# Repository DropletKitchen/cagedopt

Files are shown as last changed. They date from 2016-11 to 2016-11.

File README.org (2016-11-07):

* Microfluidics Imaging Rigs with Caged Optics

*This page describes how to build simple optics rigs for microfluidics applications based on professional-grade caged optics sytems and scientific cameras.*

This is a [[https://DropletKitchen.github.io][DropletKitchen]] project.

If not stated otherwise, the designs and documentation in this repository
is Copyright (c) 2016 Martin Fischlechner and DropletKitchen Contributors,
and made available under a
[[https://creativecommons.org/licenses/by/4.0/][Creative Commons Attribution 4.0 International (CC BY 4.0)]] License.
** Introduction
This project shows one way to package caged optics into systems with a
small footprint and highly functional design. The example here is a
simple microscope-setup for microfluidics experimentation.  Instead of
using an optics table, or an all-metal optics breadboard, a
combination of laser-cut 5mm acrylic sheets with M6 nuts and bolts are
used to assemble rigid and customized optical instruments. The system
uses a simple, magnetic kinematic design for the x,y,z-stage and a
high-power LED with cheap plastic focusing optics for illumination.
The optics is based on an infinity-corrected objective, a lens and a
global-shutter CCD or CMOS-camera to obtain videos or images. The
output of an infinity-corrected objective (they usually have an
'infinity' symbol engraved) is a parallel beam of light. It therefore
needs a lens to create an image. The advantage is that between the
objective and the lens many optic components can be placed; the design
can therefore also be used as a starting point for more complex
setups, e.g.  for measuring fluorescence. To get an idea which optics
components are available and how much they cost, have a look at the
websites of optics companies, for example Thorlabs
(https://www.thorlabs.com/navigation.cfm).

#+CAPTION: Image of the rig at several stages of the build. A] bottom plate with the optics and an LED-driver enclosed in a little box. B] plate with LED and magnets to hold the stage. This part is used to immobilise the optics by clamping. C] XYZ-stage: Z and tilt is adjusted with three optics screws. X-Y movement is controlled with an inexpensive xy-stage. D] the fully assembled rig.
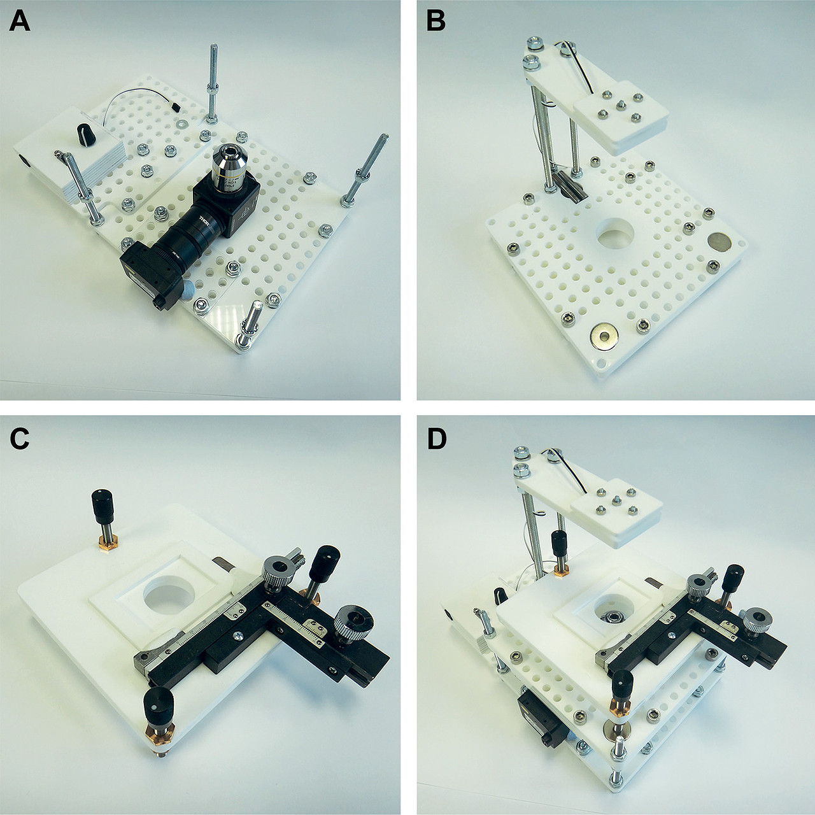
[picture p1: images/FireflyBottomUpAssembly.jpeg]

#+BEGIN_QUOTE
Image of the rig at several stages of the build. A] bottom plate with
the optics and an LED-driver enclosed in a little box. B] plate with
LED and magnets to hold the stage. This part is used to immobilise the
optics by clamping. C] XYZ-stage: Z and tilt is adjusted with three
optics screws. X-Y movement is controlled with an inexpensive
xy-stage. D] the fully assembled rig.
#+END_QUOTE

** Design
The model ([[./files/RigCageOpticsOpenSCAD.scad]]) was first developed in
openSCAD (http://www.openscad.org/) and sliced for lasercutting. Later
modifications were done in a .dxf-file with Draftsight
(http://www.3ds.com/products-services/draftsight-cad-software/free-download/). Starting
with a 3D-model is convenient to play with overall dimensions and
shapes, but the design is quicker to modify in 2D-CAD at later stages
([[./files/RigCageOpticsPartsForCutting.dxf]]). The standard fixtures for
optics on optics tables are M6, spaced 25mm apart. To have a flexible
way of mounting (additional) parts, holes of 6mm in diameter with a
spacing of 12.5mm (center to center) are additionally embedded into
the design where possible. This makes setups adaptable and extendable.

#+CAPTION: Left: 3D-model in openSCAD. Right: Parts for laser cutting.
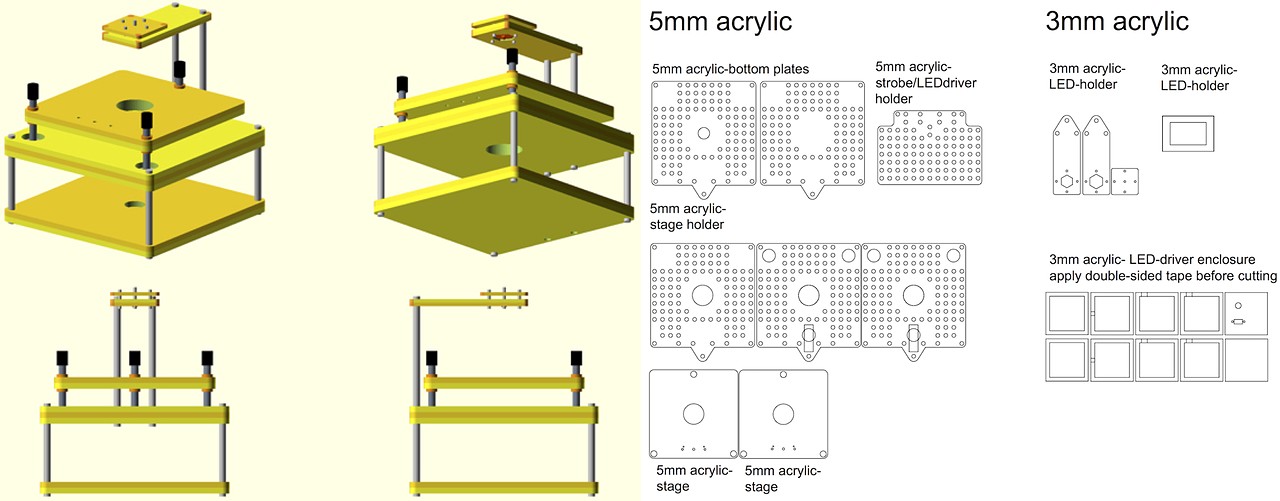
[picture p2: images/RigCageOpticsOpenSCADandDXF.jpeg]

#+BEGIN_QUOTE
Left: 3D-model in openSCAD. Right: Parts for laser cutting.
#+END_QUOTE
** Materials

| Item                                                                  |          number | bought from               | part number    | approx cost (£/euro) |
|-----------------------------------------------------------------------+-----------------+---------------------------+----------------+----------------------|
| Structural components                                                 |                 |                           |                |                      |
|-----------------------------------------------------------------------+-----------------+---------------------------+----------------+----------------------|
| M6 Hex Screws (different lengths, eg l=16,20,25,30mm for flexibility) |            many | RS or other hardware shop |                |                   NA |
| M6 Nuts, Washers, 'shake-proof washers'                               |            many | RS or other hardware shop |                |                   NA |
| M6 Threaded Rods                                                      |     4x (~100mm) | hardware shop             |                |                   NA |
| M6 Threaded Rods                                                      |     3x (~150mm) | hardware shop             |                |                   NA |
| M3 Screws, Nuts and Washers (different lengths)                       |            many | RS or other hardware shop |                |                   NA |
| 3mm Acrylic Sheet (410x280mm)                                         |     1 pack of 5 | www.techsoft.co.uk        | TAAC3-R3-5-COL |                   18 |
| 5mm Acrylic Sheet (410x280mm)                                         |     1 pack of 5 | www.techsoft.co.uk        | TAAC3-R5-5-COL |                   25 |
| Double-Sided Tape (3M, 468MP or 467MP), optional but nice to have     |               1 | RS                        | 842-1089       |                   50 |
|-----------------------------------------------------------------------+-----------------+---------------------------+----------------+----------------------|
| XYZ-stage                                                             |                 |                           |                |                      |
|-----------------------------------------------------------------------+-----------------+---------------------------+----------------+----------------------|
| Fine Adjustment Screw with Knob, 1/4"-80, 2.00" Long                  |               3 | Thorlabs                  | FAS200         |                   17 |
| Locking Phosphor-Bronze Bushing with Nut, 1/4"-80, L=0.50"            |               3 | Thorlabs                  | N80L6P         |                   21 |
| XY-stage from eBay (search 'microscope stage')                        |               1 | eBay                      |                |               max 20 |
| Eclipse 20mm Threaded Hole Neodymium Ring Magnet                      |               1 | RS                        | 792-4565       |                    7 |
| Eclipse 20mm Neodymium Disc Magnet (3 each; we use 5 for assembly)    |               2 | RS                        | 695-0184       |                   22 |
| Short Steel Rods (magnetisable) 20-40mm long, 5-6mm in diameter       |               2 | NA                        | NA             |                   NA |
|-----------------------------------------------------------------------+-----------------+---------------------------+----------------+----------------------|
| Light                                                                 |                 |                           |                |                      |
|-----------------------------------------------------------------------+-----------------+---------------------------+----------------+----------------------|
| RECOM POWER RCD-24-0.70/W/X3 LED Driver Adjustable                    |               1 | Farnell                   | 1793223        |                   13 |
| OPULENT  REBEL-STAR-ES-NW200  High Brightness LED                     |               1 | Farnell                   | 2110405        |                    4 |
| Polymer Optics 141/180, Lens Assembly                                 |               1 | RS                        | 665-6573       |                    3 |
| Stripboard, 10kOhm Potentiometer                                      |                 | eg Farnell, RS or other   |                |                   NA |
| Slide Switch, Male/Female 0.1" PCB Connectors                         |                 | eg Farnell, RS or other   |                |                   NA |
| Sugru for isolation of wire connections...                            |               1 | cpc Farnell               | MK00041        |                    6 |
| Standard Epoxy Glue                                                   |              NA |                           | NA             |                   NA |
|-----------------------------------------------------------------------+-----------------+---------------------------+----------------+----------------------|
| Optics                                                                |                 |                           |                |                      |
|-----------------------------------------------------------------------+-----------------+---------------------------+----------------+----------------------|
| RMS10X - 10X Olympus Plan Achromat Objective, 0.25 NA, 10.6 mm WD     |               1 | Thorlabs                  | RMS10X         |                  285 |
| RMS to SM1 adapter                                                    |               1 | Thorlabs                  | SM1A3TS        |                   16 |
| Cage Cube-Mounted Penta Prism                                         |               1 | Thorlabs                  | CCM1-PS932/M   |                  110 |
| LENS: F=100mm 1"diameter (cheaper) OR Achromatic Doublet f=50 mm, Ø1" |               1 | Thorlabs                  | AC254-050-A-ML |                   70 |
| 1" Lens tubes (1 adjustable + other (adjust Lens-Camera-distance))    | depends on Lens | look at Thorlabs          |                |                  ~50 |
| Adapter with External C-Mount Threads and Internal SM1 Threads        |               1 | Thorlabs                  | SM1A9          |                   14 |
| Global Shutter Camera: eg Firefly MV USB2.0 Camera (Point Grey)       |               1 | Point Grey                | FMVU-03MTM-CS  |                 ~200 |
|-----------------------------------------------------------------------+-----------------+---------------------------+----------------+----------------------|

** Assembly
*** Optics
One has an overwhelming choice of optics components. Think of which
magnification you need for the objective. To focus the image onto the
camera we use a F=50mm double achromat lens, but a simple F=100mm lens

works equally well (but needs more space). As the rig uses standard 1"
optics, any camera can be mounted with appropriate adapters. We have
chosen the FireflyMV because it uses USB 2.0, has a global shutter and
can be triggered, its image binned, etc. (Firefly MV Technical
Reference Manual, https://www.ptgrey.com/support/downloads/10116). It
runs well on Ubuntu Linux (and Win) and even on Raspberry Pi. Such
'inexpensive' scientific cameras will never give you high-speed video
(max ~ 400fps with the FireflyMV when binning to a very small image),
but bright illumination and minimising the exposure time yields sharp
images of fast events, which is good enough for most microfluidics
applications. One can enhance the camera greatly by strobing the LED
light source (see here for an example:
https://github.com/DropletKitchen/strobe).  If you need high-speed
video, you will have to use a true 'fast camera' with on-board RAM,
which start around 6k GBP (eg a Miro Phantom).

For assembly you have to first attach the lens to the camera such that
it is focused to 'infinity'. Get the camera to run on a computer,
connect the camera and lens with a tube (the distance between lens
camera-chip should equal the focal length of the lens; you will need
an adjustable SM1 lens tube in your assembly to get it right). Then
focus the image on a distant object (e.g. a tree/house outside
somewhere, or a feature in a far-away corner of the lab). Fix the
distance with a locking ring. Now connect this assembly with the 30 mm
cage containing a Penta Prism or a 45 degree mirror, screw in your
objective (with the right adapter) and you are done.

*** Structure
Assembling the rig itself is pretty straightforward; have a look at
the image above. Make sure that your components fit - if you change
the design, just measure components with a caliper and use exactly
those dimensions for holes etc. Laser cut components usually result in
a tight fit. The optics assembly is held in place by clamping it
between the bottom plate and the upper part using M6 threaded rod
posts. Use washers, or better 'shake-proof washers' where possible.

The x,y,z-stage is mounted on three optics screws with spherical ends
in a kinematic fashion - this defines the position of the stage by
resting on 6 points of contact. This is ideally 3 points on one, 2 on
the next, and one on the third. Here strong magnets are used to fix
the stage on its support - a ring magnet on the first side (a small
cheat but works well), 2 stacked disk magnets that magnetize two small
steel rods on top, and a stack of three disk magnets on the third
point.  This assembly alone allows you not only to control z distance
(focus), but you can tilt and therefore have some movement in x,y. For
convenience, adding an inexpensive x,y stage is recommended. They all
differ, so make sure you adapt the files accordingly.

*** Light
For the lightsource, a star-shaped white high power LED is used which
is controlled by an adjustable LED driver (Recom RCD-24-0.70,
http://www.recom-power.com/pdf/Lightline/RCD-24.pdf). An M3 screw acts
as a heat sink and also holds the LED in place. A potentiometer is
used to control brightness. Along with an on/off switch, the
components are soldered onto a stripboard and then packaged in an
acrylic enclosure. It does not have to bear large loads, so the
enclosure is based on cut acrylic sheets with double-sided tape added
to one side before cutting. This allows the structural components to
be bonded together.  Inexpensive plastic lenses are used to focus the
LED light onto the chip. For assembly, just use a dab of epoxy
glue. Do not use 'Superglue', as the cyanoacrylate vapours cloud the
optics components over time.  Change the distance between LED and the
stage such that the image on the camera is overexposed when the LED is
fully on and the camera is set to the smallest exposure time
possible. This allows you to get the best possible images of
fast-moving objects with your setup. Below is the circuit diagram for
wiring if you use the Recom LED-driver. If you want an on/off switch,
just wire it to the voltage or ground wire. Almost any power supply
will do (>=1A, 5-36V).

#+CAPTION: Circuit diagram for the Recom LED driver.
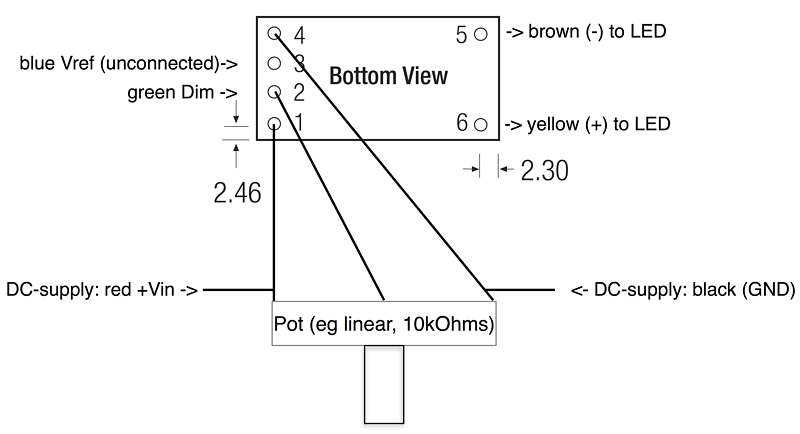
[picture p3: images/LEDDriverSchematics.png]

#+BEGIN_QUOTE
Circuit diagram for the Recom LED driver.
#+END_QUOTE

** Adapt the design to other components
It is relatively easy to adjust designs to other components. Use a
caliper to measure parts and change design files accordingly.

#+CAPTION: Rig with a Miro EX2 fast camera and an objective turret. The file for laser cut parts can be found here ([[file:./files/MiroEX2RigLasercutParts.dxf]])
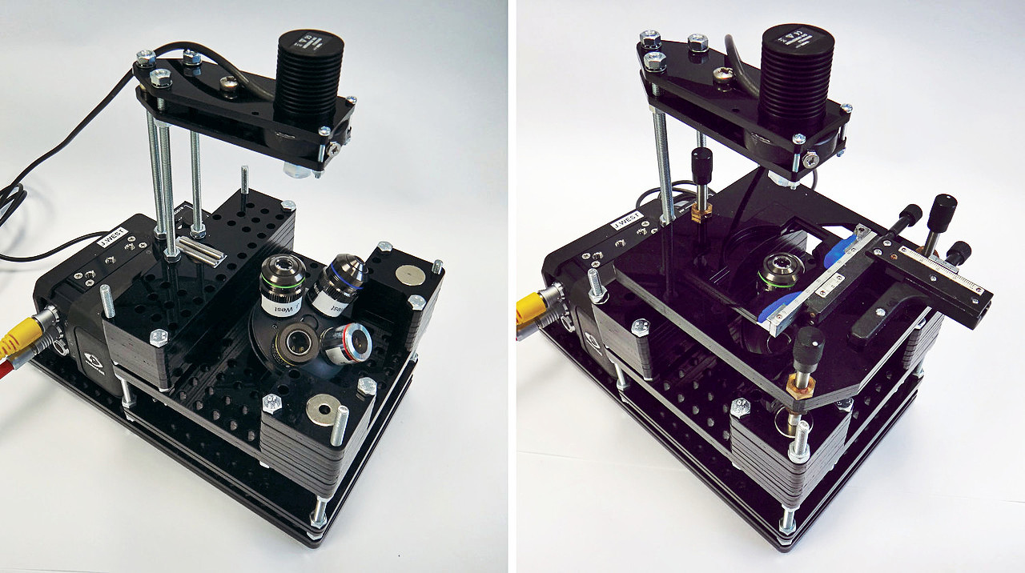
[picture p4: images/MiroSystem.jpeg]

#+BEGIN_QUOTE
Rig with a Miro EX2 fast camera and an objective turret. The file for
laser cut parts can be found here ([[./files/MiroEX2RigLasercutParts.dxf]]).
#+END_QUOTE

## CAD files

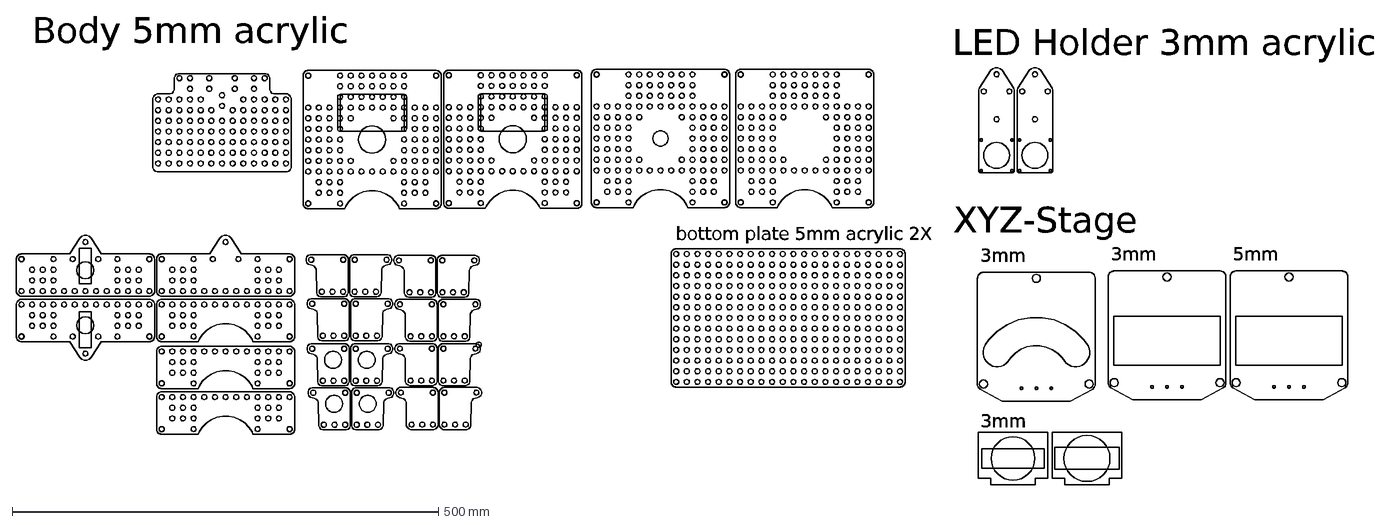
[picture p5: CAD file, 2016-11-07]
files/MiroEX2RigLasercutParts.dxf
Body 5mm acrylic
bottom plate 5mm acrylic 2X
3mm
5mm
LED Holder 3mm acrylic
XYZ-Stage

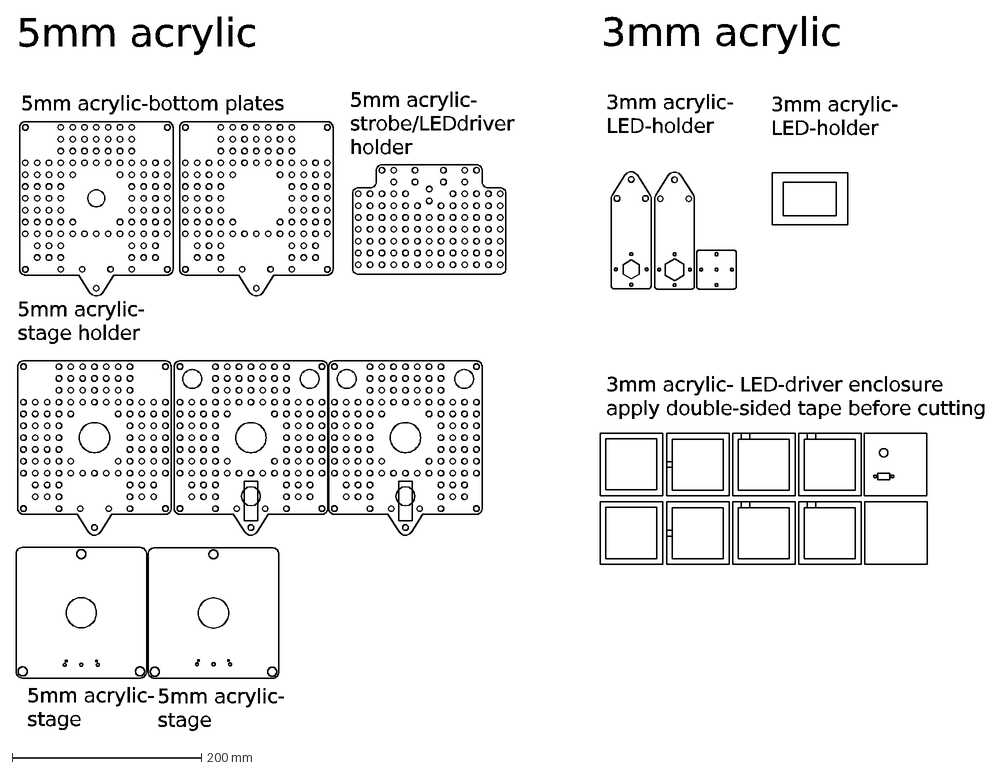
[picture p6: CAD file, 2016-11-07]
files/RigCageOpticsPartsForCutting.dxf
5mm acrylic- stage holder
5mm acrylic-bottom plates
5mm acrylic- stage
5mm acrylic- strobe/LEDdriver holder
5mm acrylic
3mm acrylic
3mm acrylic- LED-holder
3mm acrylic- LED-driver enclosure apply double-sided tape before cutting

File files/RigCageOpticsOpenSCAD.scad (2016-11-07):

/////////////////////////////
//////Simple rig/////////////
/////////////////////////////


//the parts have been sliced into sheets (for lasercutting), if you 3D print, make 'combined' .stl-files of sheet1&2 (bottom part), sheet3&4 (stage), sheet5&6 (LED holder), and sheet7 (to clamp down the LED), by compiling, rendering and exporting the parts together 

//optional parts are commented out (remove '*' to see)
// add '#' to highlight part/subtraction in red (useful to find and investigate parts) 

////////////////////////////////////////////////////
//VARIABLES - change them according to your needs //
////////////////////////////////////////////////////

roundness_dia = 6;//bottom part: radius of rounded edges (should be bigger than radius screws: M6>3)
roundness_dia2 = 7;//xyz-stage, take care for it being big enough for leadscrews and wall
roundness_dia3 = 3;//roundness of lightfixtures
//
x=75;//x-dimension of screwholes (stands) of bottom plate in mm; min size required for fitting our x/y stage in is around x= 70mm
z=5; //sheet thickness if you use a laser cutter
zLED=3; //sheet thickness LED and lens fixture, again, for lasercutting
min_wallsize = 0;//distance between cut holes and part outlines, use >=3 when using M6 screws to accomodate the nuts, only used in lightfixtures, quite obsolete right now
prop=5;//proportion x:light fixture holes

//variables for kinematic stage
radius_centerhole1 = 16; // r of centerhole_stage, bottom plate
radius_centerhole2 = 16; // r of centerhole_stage, top plate

radius_screws = 3; //radius of screws used (default M6)
radius_leadscrewnut = 4.8; //radius of leadscrew-nut for z-stage


diameter_steelbar = 6; // diameter for steelbar-inserts, kinematic stage
radius_magnet = 10; //radius of magnets used for kinematic stage

y=(x-radius_screws-radius_magnet);//dimension (leadscrew-holes) of stage

stage_height = 30; //height of stage (just for drawing)
light_height = 100; //height of light fixture (just for drawing)
screw_connector1_height = 85; //height of screw connector1 (just for drawing), optional part (commented out)
screw_connector2_height = 70; //height of screw connector2 (just for drawing), optional part (commented out)

//Light fixture variables
LED_radius = 11.5; //half of the LED diameter
makesmaller = 1.5; //hole for LED to sit on (must be smaller than LED diameter)
LED_radius1 = LED_radius - makesmaller;
radius_LEDscrews = 1.5; //radius of screws on LED part (defaultM3)

//lens fixture variables (optional parts if you want to use a standard optics lens to focus the light onto the sample, commented out)
radius_LENS = 6.5; //radius of collimating lens used (1/2-inch optics)
indent_LENS = 1; //make radius smaller for parts that hold lens in place

//optional mounted xy-stage: variables
xystagemiddleholedistance = 55;//check your stage and figure out where/how to mount
xystagemiddleholeradius = 1.75;
xystageoffcenterholedistance = 55;
xystageoffcenterholeoffset = 17.5;
xystageoffcenterholeradius = 1.5;

//variables for illustration of added hardware
radius_leadscrew = 3.14;

//////////////////////////////////////////////////////////////////////////////////////////////////////////////
/////////////////SHEET 0/-2 - (used for cage systems and PS3-systems as bottom sheet (instead of sheet 1)/////
//////////////////////////////////////////////////////////////////////////////////////////////////////////////
translate ([0,0,-12*z])
difference ()
{

$fn=50;
   color ("yellow", a=1.0)
   translate ([0,0,0])
   hull()
   {
        translate ([x,x,0])
        cylinder(r = roundness_dia, h = z, $fa=1, $fs=0.5, center = true);
        translate ([-x,x,0])
        cylinder(r = roundness_dia, h = z, $fa=1, $fs=0.5, center = true);
        translate ([x,-x,0])
        cylinder(r = roundness_dia, h = z, $fa=1, $fs=0.5, center = true);
        translate ([-x,-x,0])
        cylinder(r = roundness_dia, h = z, $fa=1, $fs=0.5, center = true);
   }

//screwholes
//top right
translate ([x, x, -z]) 
cylinder(r = radius_screws, h = 2*z, $fa=1, $fs=0.5);
//top left
translate ([-x, x, -z]) 
cylinder(r = radius_screws, h = 2*z, $fa=1, $fs=0.5);
//bottom right
translate ([x, -x, -z]) 
cylinder(r = radius_screws, h = 2*z, $fa=1, $fs=0.5);
//bottom left
translate ([-x, -x, -z]) 
cylinder(r = radius_screws, h = 2*z, $fa=1, $fs=0.5);

//screwholes for light-fixture
//top right
translate ([x/prop, x, -z]) 
cylinder(r = radius_screws, h = 2*z, $fa=1, $fs=0.5);
//top left
translate ([-x/prop, x, -z]) 
cylinder(r = radius_screws, h = 2*z, $fa=1, $fs=0.5);
}


//////////////////////////////////////////////////////////////////////////////////////////////////////////////
/////////////////SHEET 0/-1 - (used for cage systems only)///////////////////////
//////////////////////////////////////////////////////////////////////////////////////////////////////////////
translate ([0,0,-11*z])
difference ()
{

$fn=50;
   color ("gold", a=1.0)
   translate ([0,0,0])
   hull()
   {
        translate ([x,x,0])
        cylinder(r = roundness_dia, h = z, $fa=1, $fs=0.5, center = true);
        translate ([-x,x,0])
        cylinder(r = roundness_dia, h = z, $fa=1, $fs=0.5, center = true);
        translate ([x,-x,0])
        cylinder(r = roundness_dia, h = z, $fa=1, $fs=0.5, center = true);
        translate ([-x,-x,0])
        cylinder(r = roundness_dia, h = z, $fa=1, $fs=0.5, center = true);
   }

//centerhole
translate ([0, 0, -z]) 
cylinder(r = 3*radius_screws, h = 2*z, $fa=1, $fs=0.5);

//screwholes
//top right
translate ([x, x, -z]) 
cylinder(r = radius_screws, h = 2*z, $fa=1, $fs=0.5);
//top left
translate ([-x, x, -z]) 
cylinder(r = radius_screws, h = 2*z, $fa=1, $fs=0.5);
//bottom right
translate ([x, -x, -z]) 
cylinder(r = radius_screws, h = 2*z, $fa=1, $fs=0.5);
//bottom left
translate ([-x, -x, -z]) 
cylinder(r = radius_screws, h = 2*z, $fa=1, $fs=0.5);
}

/////////////////////////////////////////////////////////////
/////////////////SHEET1 (bottom part)///////////////////////
////////////////////////////////////////////////////////////

difference ()
{

$fn=50;
   color ("yellow", a=1.0)
   translate ([0,0,0])
   hull()
   {
        translate ([x,x,0])
        cylinder(r = roundness_dia, h = z, $fa=1, $fs=0.5, center = true);
        translate ([-x,x,0])
        cylinder(r = roundness_dia, h = z, $fa=1, $fs=0.5, center = true);
        translate ([x,-x,0])
        cylinder(r = roundness_dia, h = z, $fa=1, $fs=0.5, center = true);
        translate ([-x,-x,0])
        cylinder(r = roundness_dia, h = z, $fa=1, $fs=0.5, center = true);
   }

//centerhole
translate ([0, 0, -z]) 
cylinder(r = radius_centerhole1, h = 2*z, $fa=1, $fs=0.5);

//screwholes
//top right
translate ([x, x, -z]) 
cylinder(r = radius_screws, h = 2*z, $fa=1, $fs=0.5);
//top left
translate ([-x, x, -z]) 
cylinder(r = radius_screws, h = 2*z, $fa=1, $fs=0.5);
//bottom right
translate ([x, -x, -z]) 
cylinder(r = radius_screws, h = 2*z, $fa=1, $fs=0.5);
//bottom left
translate ([-x, -x, -z]) 
cylinder(r = radius_screws, h = 2*z, $fa=1, $fs=0.5);

//screwholes for light-fixture
//top right
translate ([x/prop, x, -z]) 
cylinder(r = radius_screws, h = 2*z, $fa=1, $fs=0.5);
//top left
translate ([-x/prop, x, -z]) 
cylinder(r = radius_screws, h = 2*z, $fa=1, $fs=0.5);
}

/////////////////////////////////////////////////////////////////////
////SHEET2 (bottom part, second layer with steel bars)//////////////
////////////////////////////////////////////////////////////////////

difference ()
{

$fn=50;
   color ("gold", a=1.0)
   translate ([0,0,z])
   hull()
   {
        translate ([x,x,0])
        cylinder(r = roundness_dia, h = z, $fa=1, $fs=0.5, center = true);
        translate ([-x,x,0])
        cylinder(r = roundness_dia, h = z, $fa=1, $fs=0.5, center = true);
        translate ([x,-x,0])
        cylinder(r = roundness_dia, h = z, $fa=1, $fs=0.5, center = true);
        translate ([-x,-x,0])
        cylinder(r = roundness_dia, h = z, $fa=1, $fs=0.5, center = true);
   }
//centerhole
translate ([0, 0, 0]) 
cylinder(r = radius_centerhole1, h = 2*z, $fa=1, $fs=0.5);

//screwholes
//top right
translate ([x, x, 0]) 
cylinder(r = radius_screws, h = 2*z, $fa=1, $fs=0.5);
//top left
translate ([-x, x, 0]) 
cylinder(r = radius_screws, h = 2*z, $fa=1, $fs=0.5);
//bottom right
translate ([x, -x, 0]) 
cylinder(r = radius_screws, h = 2*z, $fa=1, $fs=0.5);
//bottom left
translate ([-x, -x, 0]) 
cylinder(r = radius_screws, h = 2*z, $fa=1, $fs=0.5);

//screwholes for light-fixture
//top right
translate ([x/prop, x, 0]) 
cylinder(r = radius_screws, h = 2*z, $fa=1, $fs=0.5);
//top left
translate ([-x/prop, x, 0]) 
cylinder(r = radius_screws, h = 2*z, $fa=1, $fs=0.5);

//magnet-inserts
//bottom right
translate ([y, -y, z]) 
rotate([0, 0, 90])
cylinder(h = 2*z, r=radius_magnet, $fa=1, $fs=0.5,center = true);

//bottom left
translate ([-y, -y, z]) 
rotate([0, 0, -90])
cylinder(h = 2*z, r=radius_magnet, $fa=1, $fs=0.5,center = true);
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
